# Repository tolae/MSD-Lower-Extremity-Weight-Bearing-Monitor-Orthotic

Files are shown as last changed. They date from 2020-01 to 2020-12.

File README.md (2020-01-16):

# MSD Lower Extremity Weight Bearing Monitor Orthotic

## Overview
Individuals with injury to the lower extremities often go through a type of physical therapy called gait training in which the ability to stand and walk may be improved. Depending on pain control and prescribed weight bearing status (non, toe touch, touchdown, partial, and full/weight bearing as tolerated), patients will gradually place more weight on the injured leg. However, at this time physical therapists have little ability to measure exactly how much weight a patient is bearing.
 
Many orthopedic patients who are recently going through the gait training process struggle with controlling how much weight to bear on a leg recovering from injury. Without proper monitoring, patients often exceed their prescribed weight bearing status which could result in delayed healing, further injury, added frustration, and added financial burden. Determining whether a patient is truly compliant to their weight bearing orders can be difficult for doctors, physical therapists, and patients without accurate readings and progress of the injury. The device proposed here would allow for improved accuracy and weight bearing compliance of the patient’s lower extremities. This could also improve patient motivation and frustration, as progress should be tracked and maintained much more easily.
 
There has been no prior work done with this project.
 
This project would aim to develop and build a working orthotic prototype which could improve the weight bearing compliance and accuracy for leg orthotics while notifying the patient with alerts on whether they are putting too much weight on their foot during therapy.  Notification will also be relayed to the Physical Therapist such that they can direct the patient regarding weight bearing during the physical therapy process.  
 
Strong Memorial Hospital would like their physical therapy staff to be able to use this product with their orthopedic patients during physical therapy sessions within the acute care setting. This will allow physical therapists to more accurately educate patients regarding their weight bearing status, improving patient compliance and decreasing risk of complications after injury.

## Sponsers
Strong Memorial Hospital<br/>
Austin Crane<br/>
Alyssa Reome<br/>

## Workers
Braedon Williams, Bio-Medical Engineer, bpw3109@rit.edu<br/>
Daniel Capra, Eletrical Engineer, dac3781@rit.edu<br/>
Kevin Jones, Industrial Systems Engineer, kmj2243@rit.edu<br/>
Raphael Luo, Eletrical Engineer, jxl6725@rit.edu<br/>
Ethan Tola, Computer Engineer, ext9285@rit.edu<br/>

## Documentation
Documentation for this project can be found on (Confluence)[https://wiki.rit.edu/display/P20016/Project+Overview]. This is a live wiki page that is under construction.

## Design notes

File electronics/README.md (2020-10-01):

# MSD Eletronic Files
All the schematics and designs were done using Cadence Orcad 17.2. The files
in this directory was put under source control for ease of multi-tasking and
reducing the number of redudant work to make the same custom footprints.

## Important Directiories
 - <b>custom_parts</b>: Contains the custom components and pcb footprints
 required for layout.
 - <b>extenstion_1</b>: Contains the schematic and layout focusing on the first
 extenstion for the footpad.
 - <b>imported_parts</b>: Contains footprints and pads for external components
 such as the TMUX1109.
 - <b>main</b>: Contains the schematic and layout focusing on the primary
 footpad that will interface directly with the Arduino Nano.
 - <b>wiring_complete</b>: Contains the schematics for a complete wiring
 diagram of both the Arduino Nano and the Arduino Mega. This cannot be used for
 layout as there are no footprints associated with the parts.

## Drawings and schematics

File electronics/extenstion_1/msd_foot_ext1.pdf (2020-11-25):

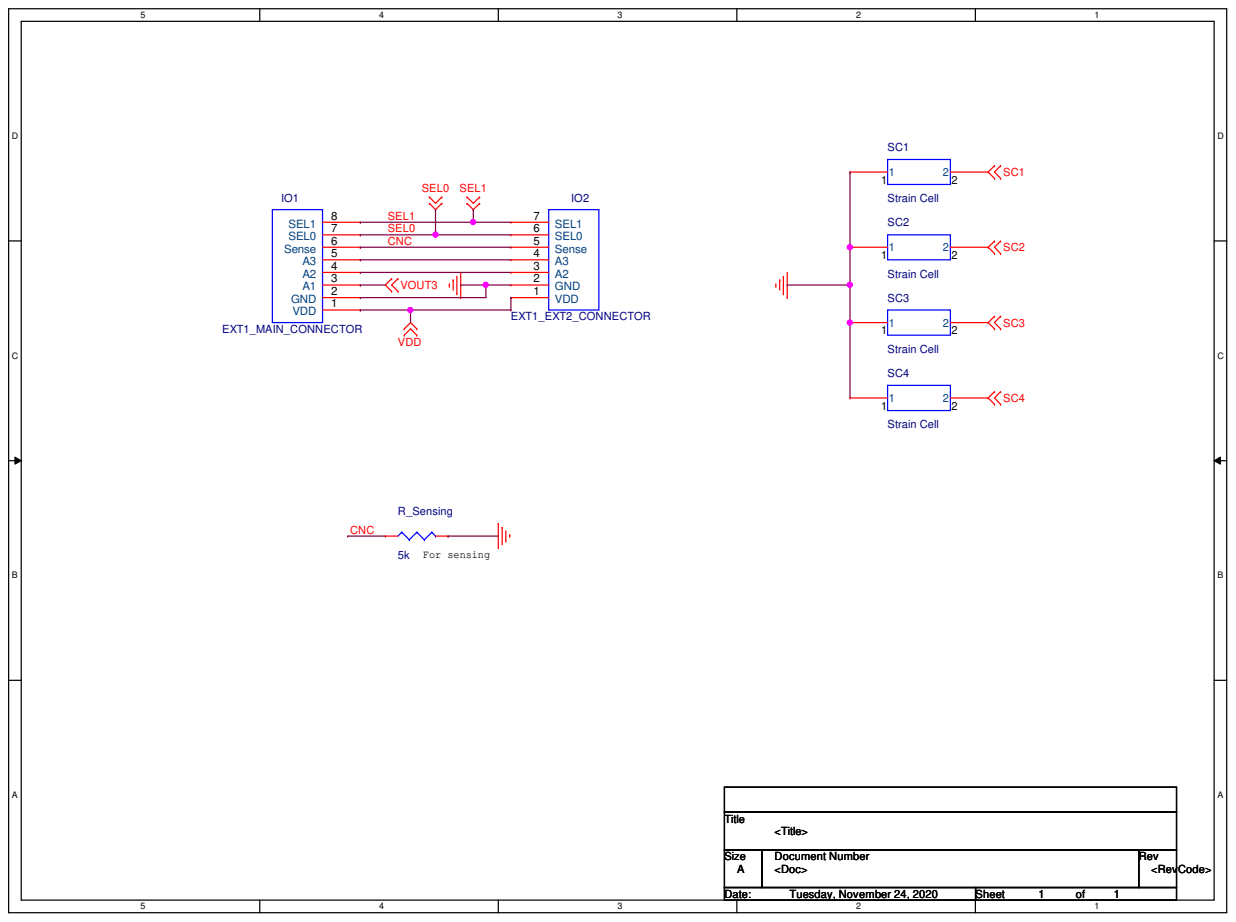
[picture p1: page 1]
For sensing; VDD; VOUT3; SEL0 SEL1; Title; Size; Document Number; Rev; Date:; Sheet; <Doc>; <RevCode>; <Title>; 1Tuesday, November 24, 2020; Strain Cell; EXT1_EXT2_CONNECTOR; Sense 5; GND 2; SEL0 6; SEL1 7; VDD 1; EXT1_MAIN_CONNECTOR; 1 GND; 5 Sense; 6 SEL0; 7 SEL1; R_Sensing; CNC; SEL1 SEL0 CNC

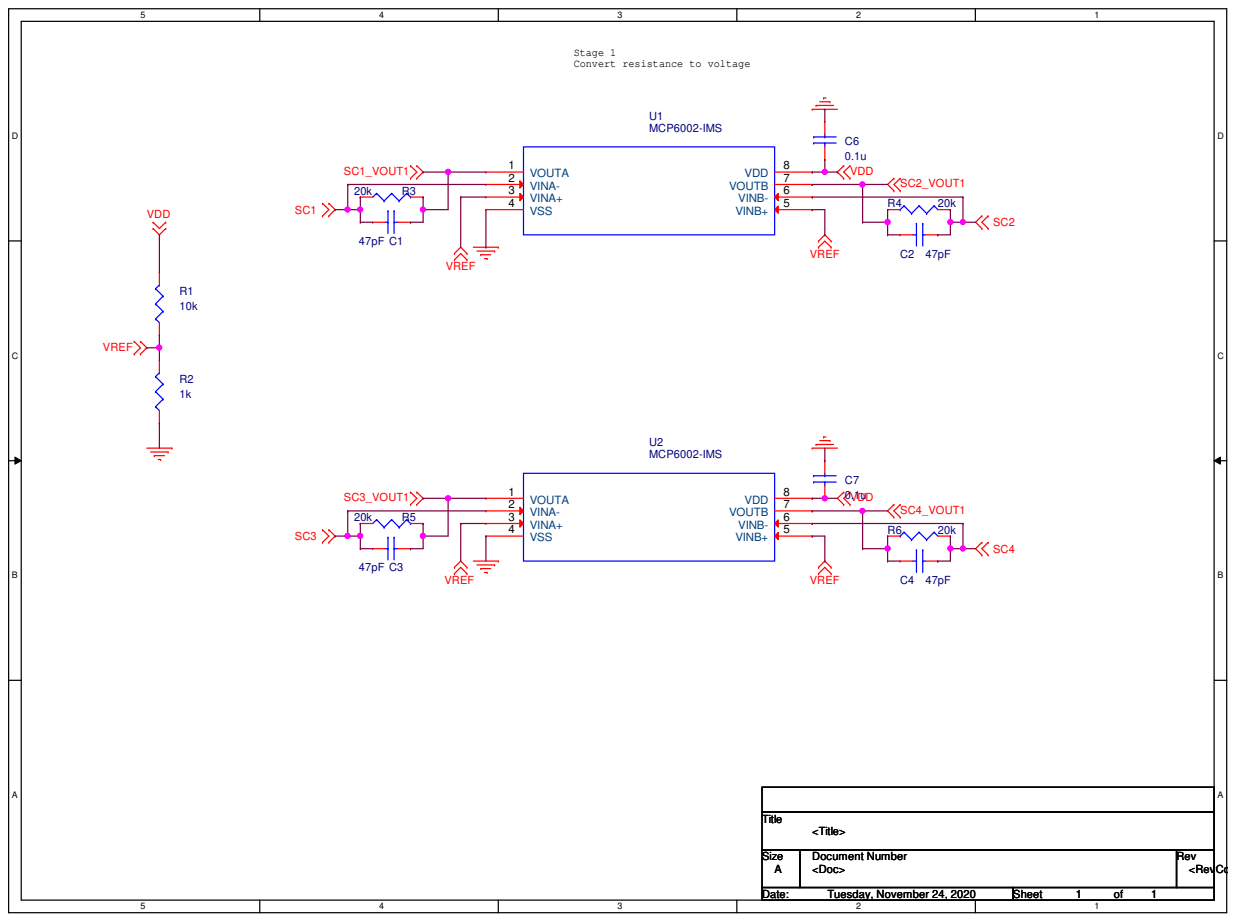
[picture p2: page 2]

Stage 1
Convert resistance to voltage

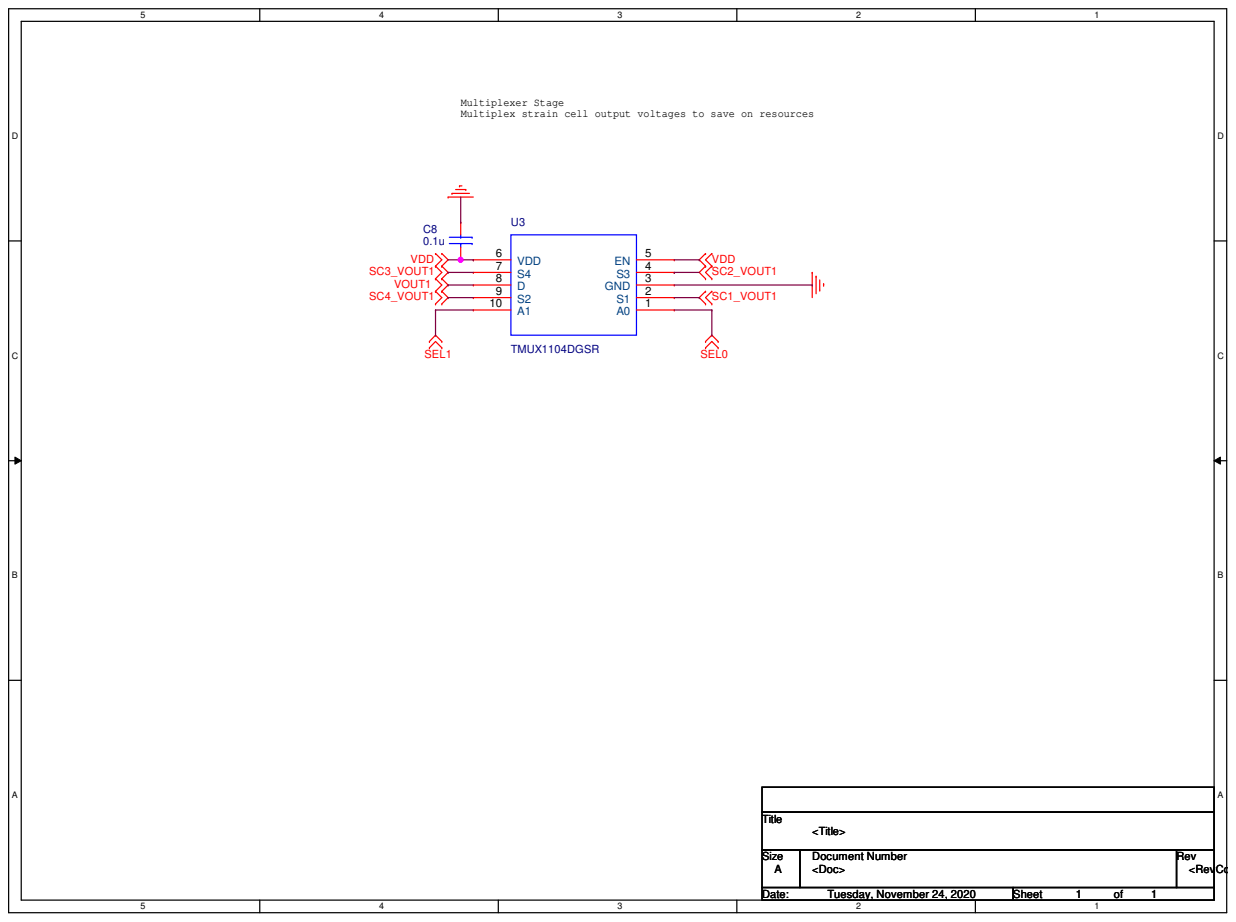
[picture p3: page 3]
SC1_VOUT1; SC2_VOUT1; SC4_VOUT1; SC3_VOUT1; VDD; SEL1; SEL0; VOUT1; Title; Size; Document Number; Rev; Date:; Sheet; <Doc>; <RevCo; <Title>; 1Tuesday, November 24, 2020; TMUX1104DGSR; 2 GND; 5 VDD 6

Multiplexer Stage
Multiplex strain cell output voltages to save on resources

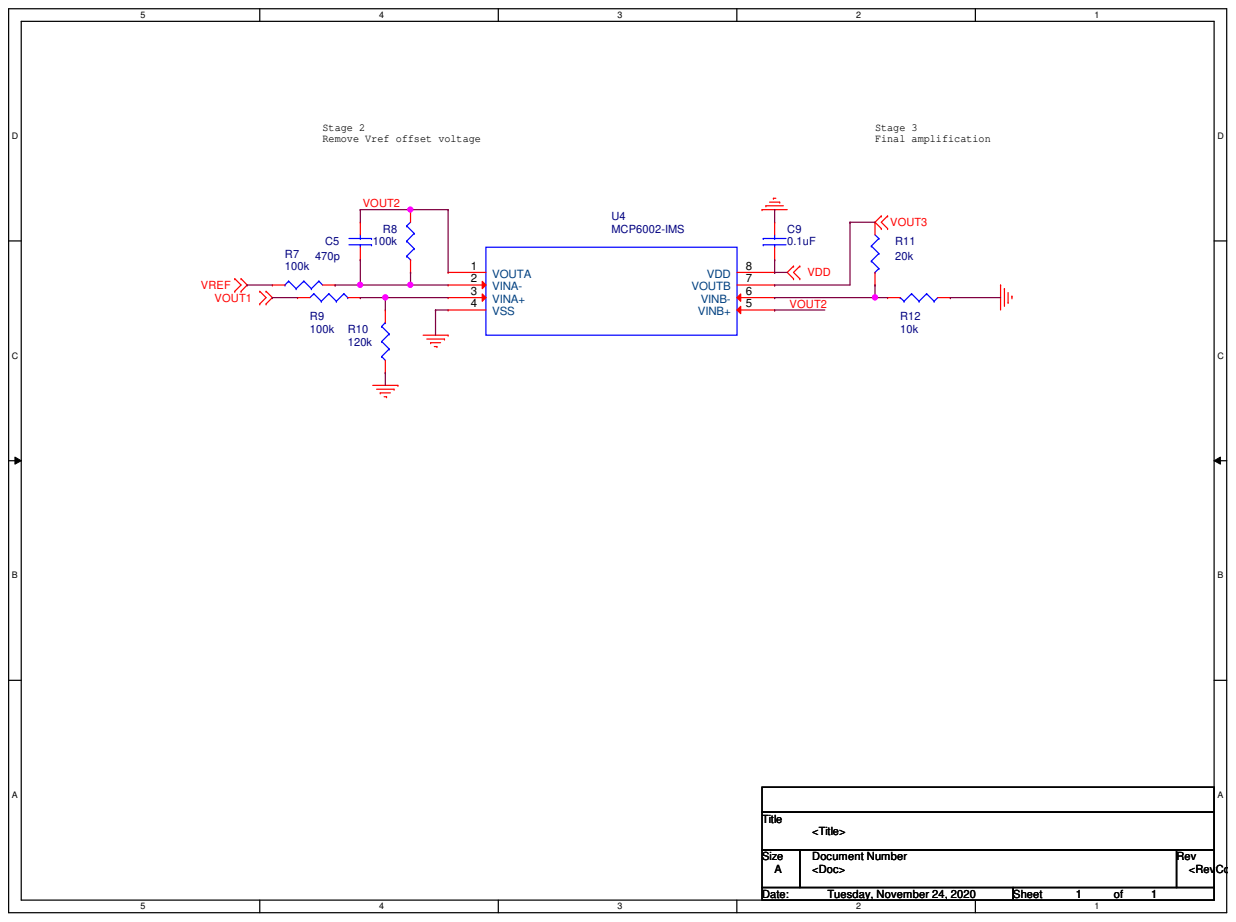
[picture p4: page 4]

Stage 2
Remove Vref offset voltage

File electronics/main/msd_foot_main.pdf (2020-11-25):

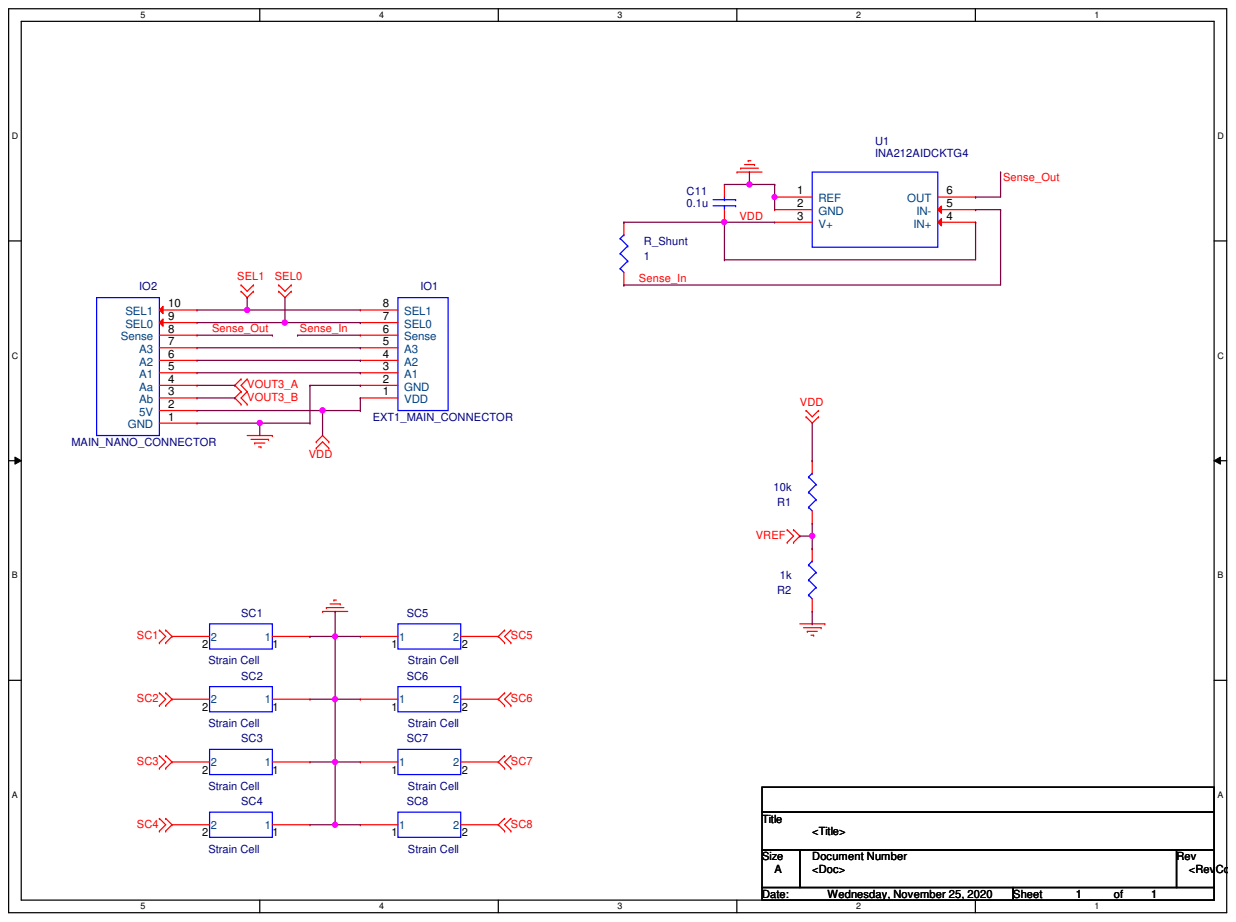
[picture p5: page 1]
VOUT3_B; VOUT3_A; SEL1 SEL0; VDD; VREF; Title; Size; Document Number; Rev; Date:; Sheet; <Doc>; <RevCo; <Title>; 1Wednesday, November 25, 2020; Strain Cell; U1 INA212AIDCKTG4; REF 1 GND 2; 5 OUT; MAIN_NANO_CONNECTOR; GND; 7 Sense; 8 SEL0; 9 SEL1; EXT1_MAIN_CONNECTOR; VDD 1; GND 2; Sense 6; SEL0 7; SEL1 8; R_Shunt 1; Sense_Out; Sense_In

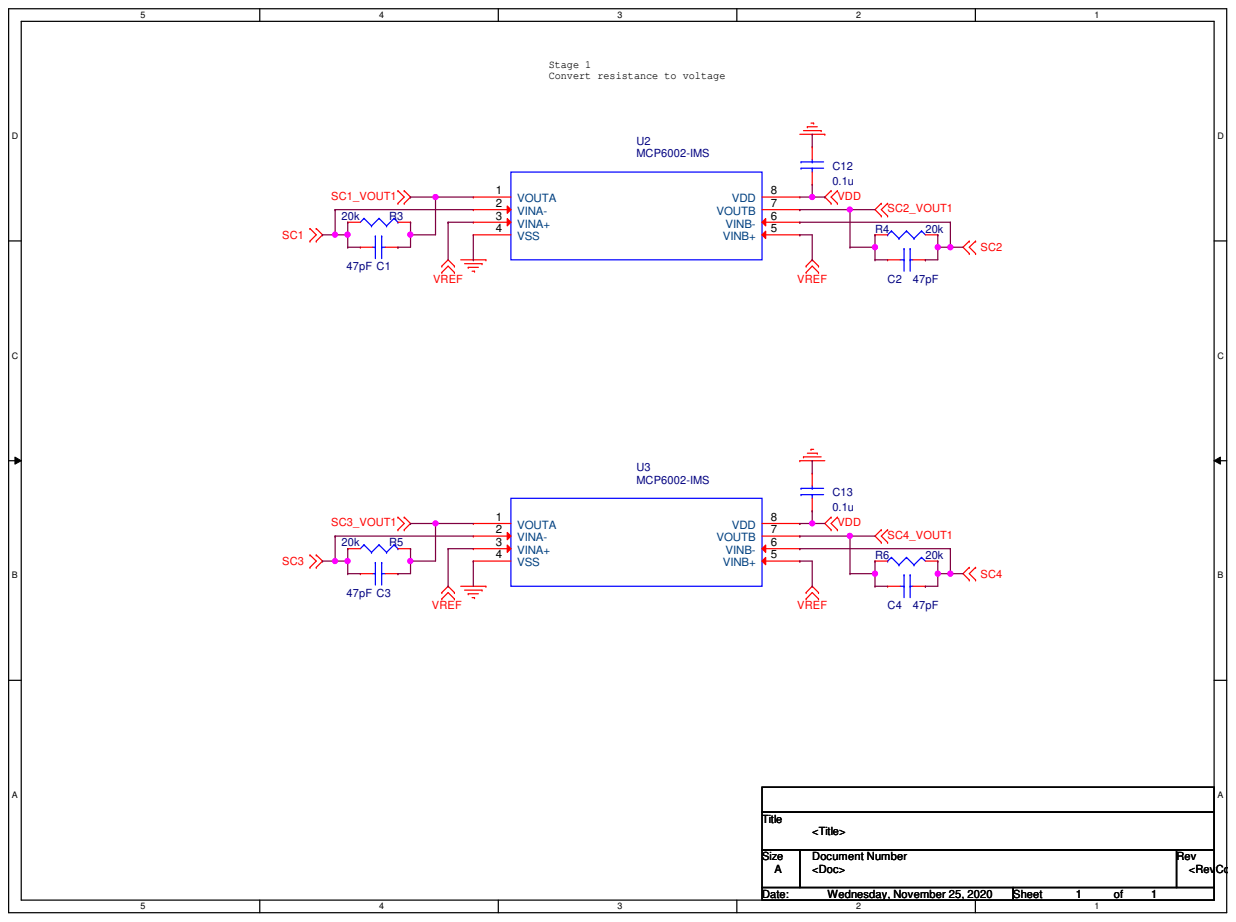
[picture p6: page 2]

Stage 1
Convert resistance to voltage

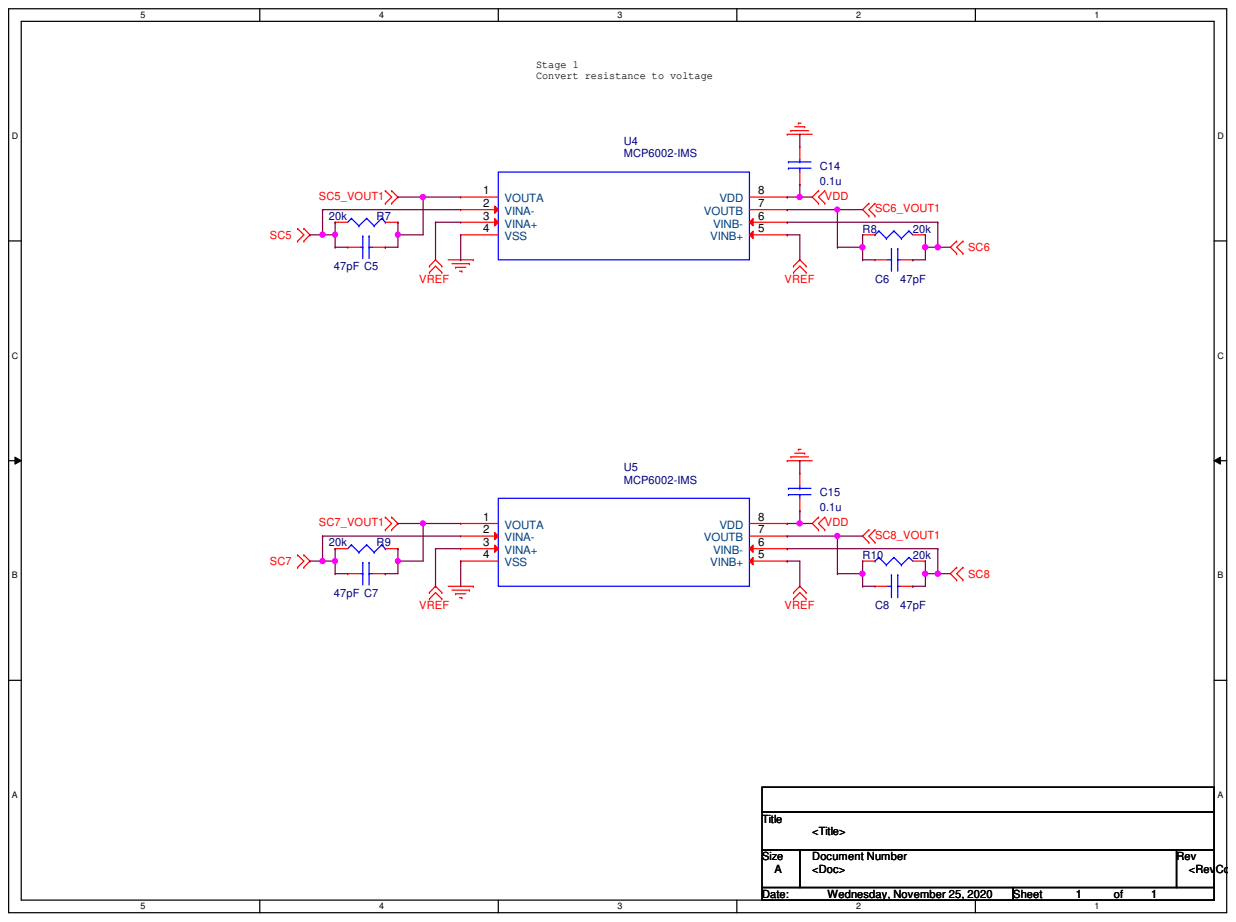
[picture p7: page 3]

Stage 1
Convert resistance to voltage

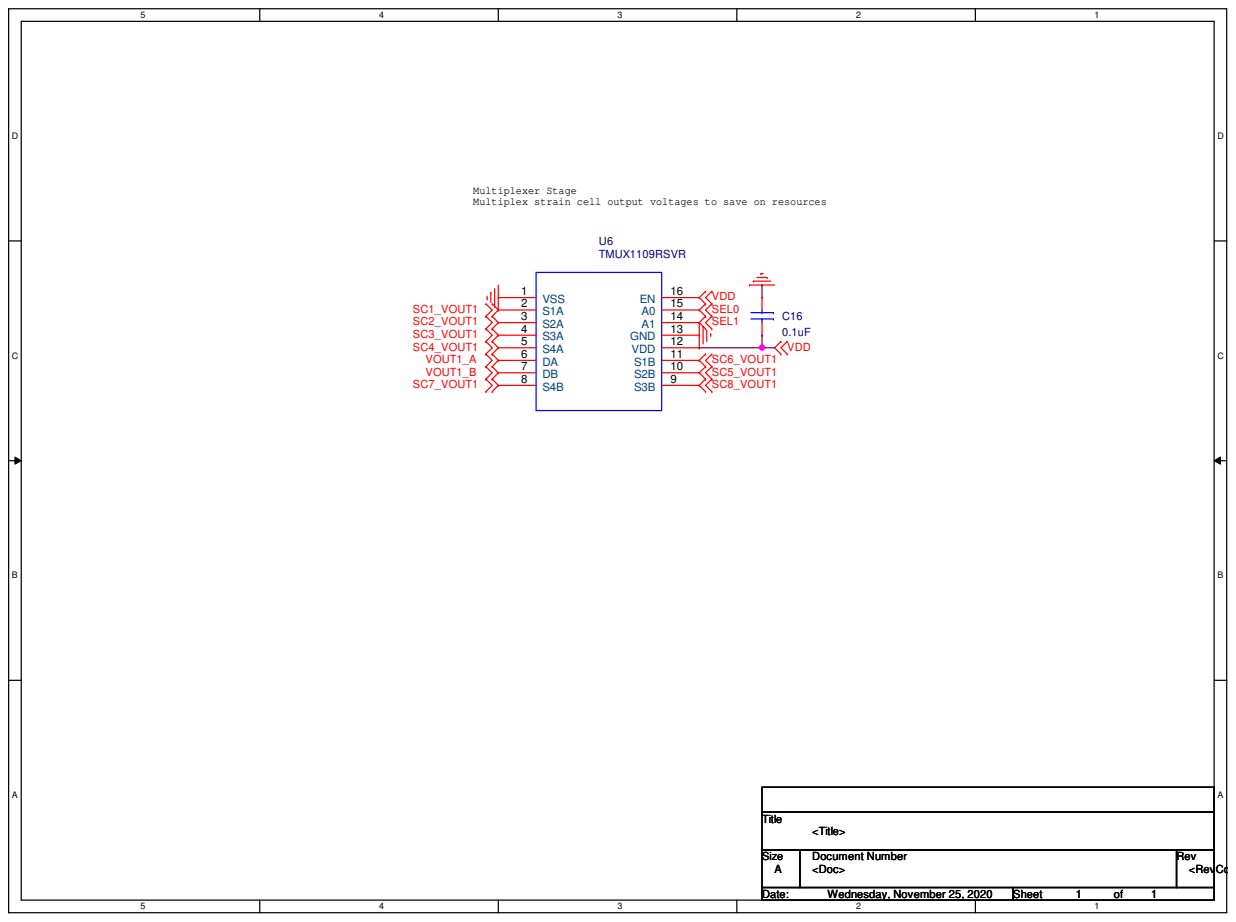
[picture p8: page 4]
SC1_VOUT1; SC6_VOUT1; SC2_VOUT1; SC5_VOUT1; SC3_VOUT1; SC8_VOUT1; SC4_VOUT1; SC7_VOUT1; SEL0 SEL1; VOUT1_B; VOUT1_A; VDD; Title; Size; Document Number; Rev; Date:; Sheet; <Doc>; <RevCo; <Title>; 1Wednesday, November 25, 2020; U6 TMUX1109RSVR; VSS 1 S1A 2 S2A 3 S3A 4 S4A 5 DA 6 DB 7; 11 VDD; 12 GND

Multiplexer Stage
Multiplex strain cell output voltages to save on resources

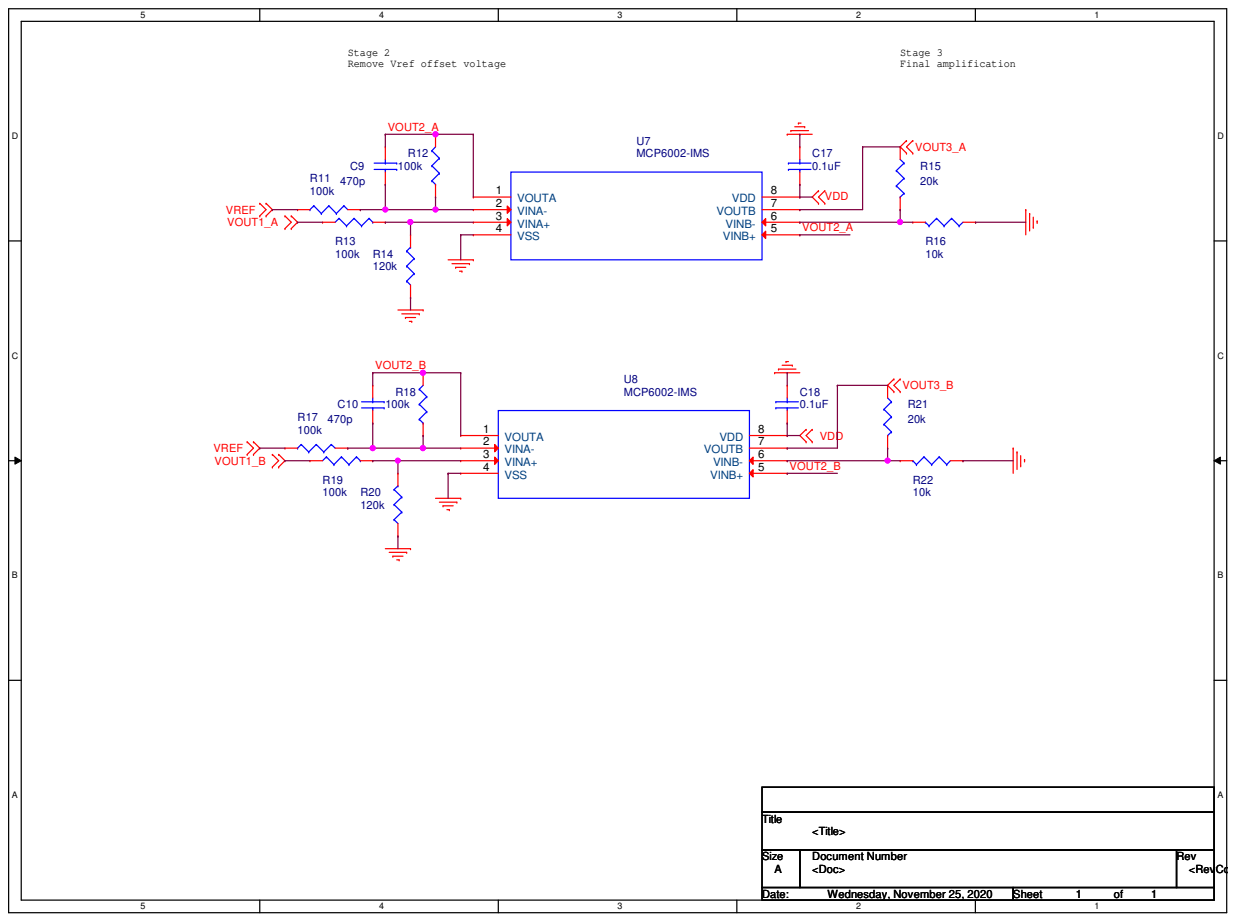
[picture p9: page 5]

Stage 2
Remove Vref offset voltage

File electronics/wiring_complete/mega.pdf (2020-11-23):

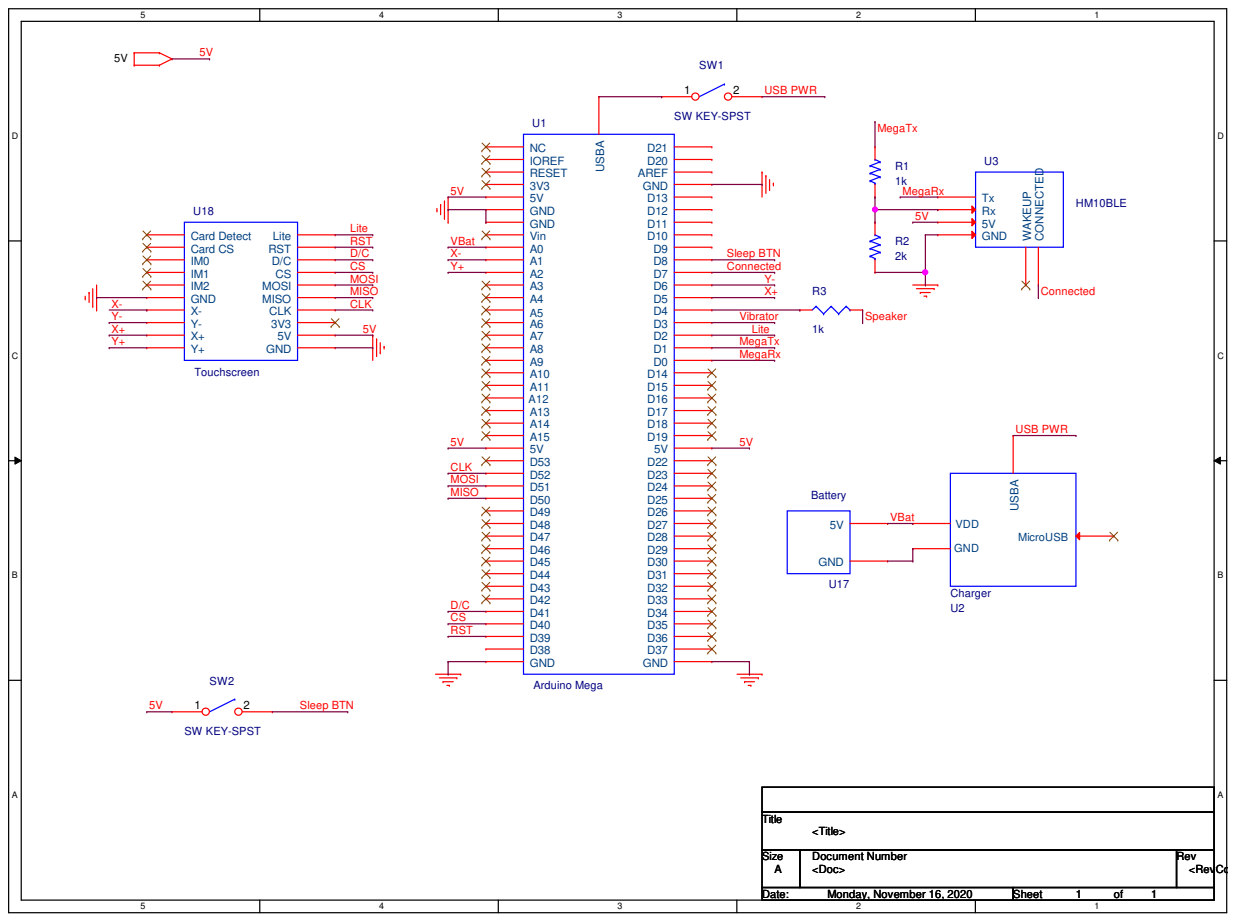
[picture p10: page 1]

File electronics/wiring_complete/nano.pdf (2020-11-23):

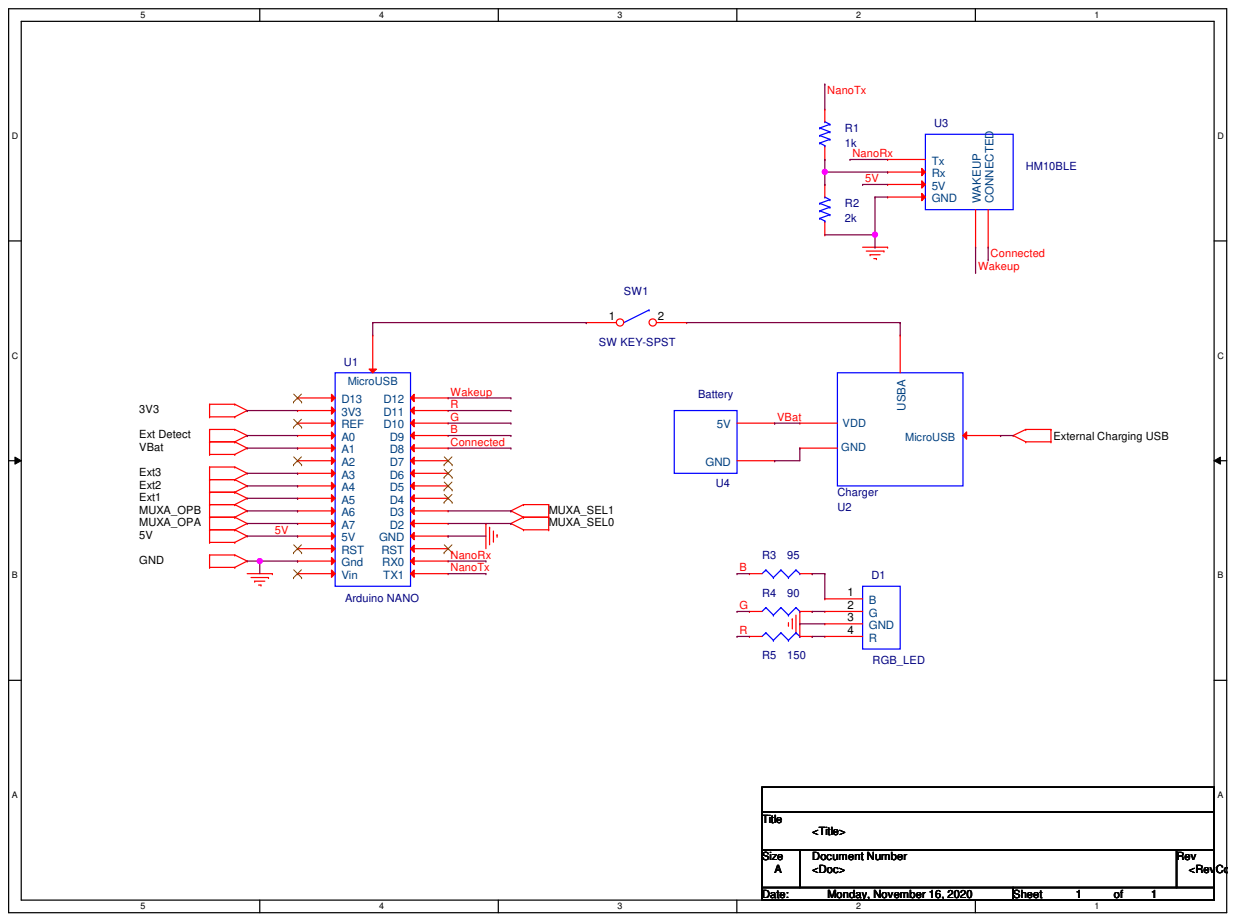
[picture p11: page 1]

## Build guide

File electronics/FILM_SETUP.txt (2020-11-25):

axlFilmCreate( "OUTLINE" ?negative nil ?undefineLineWidth 0.1270 ?sequence 12 
	?rotation 0 ?xOffset 0.0000 ?yOffset 0.0000 ?shapeBoundingBox 2.5400 ?mirrored nil ?fullContact nil 
	?suppressUnconnectPads nil ?drawMissingPadApertures nil ?useApertureRotation nil 
	?suppressShapeFill nil ?vectorBasedPad t ?drawHolesOnly nil 
	?domains '(ipc2581 pdf artwork visibility ) ?ipc2581 '() 
	?layers '("BOARD GEOMETRY/DESIGN_OUTLINE" ))
axlFilmCreate( "SILKSCREEN_TOP" ?negative nil ?undefineLineWidth 0.1270 ?sequence 11 
	?rotation 0 ?xOffset 0.0000 ?yOffset 0.0000 ?shapeBoundingBox 2.5400 ?mirrored nil ?fullContact nil 
	?suppressUnconnectPads nil ?drawMissingPadApertures nil ?useApertureRotation nil 
	?suppressShapeFill nil ?vectorBasedPad t ?drawHolesOnly nil 
	?domains '(ipc2581 pdf artwork visibility ) ?ipc2581 '(doc ) 
	?layers '("REF DES/SILKSCREEN_TOP" "PACKAGE GEOMETRY/SILKSCREEN_TOP" "COMPONENT VALUE/SILKSCREEN_TOP" "BOARD GEOMETRY/SILKSCREEN_TOP" "BOARD GEOMETRY/DESIGN_OUTLINE" ))
axlFilmCreate( "PASTEMASK_BOT" ?negative nil ?undefineLineWidth 0.1270 ?sequence 10 
	?rotation 0 ?xOffset 0.0000 ?yOffset 0.0000 ?shapeBoundingBox 2.5400 ?mirrored nil ?fullContact nil 
	?suppressUnconnectPads nil ?drawMissingPadApertures nil ?useApertureRotation nil 
	?suppressShapeFill nil ?vectorBasedPad t ?drawHolesOnly nil 
	?domains '(ipc2581 pdf artwork visibility ) ?ipc2581 '(soldermask ) 
	?layers '("VIA CLASS/PASTEMASK_BOTTOM" "PIN/PASTEMASK_BOTTOM" "PACKAGE GEOMETRY/PASTEMASK_BOTTOM" "DRC ERROR CLASS/PASTEMASK_BOTTOM" "BOARD GEOMETRY/DESIGN_OUTLINE" ))
axlFilmCreate( "SOLDERMASK_BOT" ?negative nil ?undefineLineWidth 0.1270 ?sequence 9 
	?rotation 0 ?xOffset 0.0000 ?yOffset 0.0000 ?shapeBoundingBox 2.5400 ?mirrored nil ?fullContact nil 
	?suppressUnconnectPads nil ?drawMissingPadApertures nil ?useApertureRotation nil 
	?suppressShapeFill nil ?vectorBasedPad t ?drawHolesOnly nil 
	?domains '(ipc2581 pdf artwork visibility ) ?ipc2581 '(soldermask ) 
	?layers '("VIA CLASS/SOLDERMASK_BOTTOM" "PIN/SOLDERMASK_BOTTOM" "PACKAGE GEOMETRY/SOLDERMASK_BOTTOM" "DRC ERROR CLASS/SOLDERMASK_BOTTOM" "BOARD GEOMETRY/SOLDERMASK_BOTTOM" "BOARD GEOMETRY/DESIGN_OUTLINE" ))
axlFilmCreate( "PASTEMASK_TOP" ?negative nil ?undefineLineWidth 0.1270 ?sequence 8 
	?rotation 0 ?xOffset 0.0000 ?yOffset 0.0000 ?shapeBoundingBox 2.5400 ?mirrored nil ?fullContact nil 
	?suppressUnconnectPads nil ?drawMissingPadApertures nil ?useApertureRotation nil 
	?suppressShapeFill nil ?vectorBasedPad t ?drawHolesOnly nil 
	?domains '(ipc2581 pdf artwork visibility ) ?ipc2581 '(soldermask ) 
	?layers '("VIA CLASS/PASTEMASK_TOP" "PIN/PASTEMASK_TOP" "PACKAGE GEOMETRY/PASTEMASK_TOP" "DRC ERROR CLASS/PASTEMASK_TOP" "BOARD GEOMETRY/DESIGN_OUTLINE" ))
axlFilmCreate( "SOLDERMASK_TOP" ?negative nil ?undefineLineWidth 0.1270 ?sequence 7 
	?rotation 0 ?xOffset 0.0000 ?yOffset 0.0000 ?shapeBoundingBox 2.5400 ?mirrored nil ?fullContact nil 
	?suppressUnconnectPads nil ?drawMissingPadApertures nil ?useApertureRotation nil 
	?suppressShapeFill nil ?vectorBasedPad t ?drawHolesOnly nil 
	?domains '(ipc2581 pdf artwork visibility ) ?ipc2581 '(soldermask ) 
	?layers '("VIA CLASS/SOLDERMASK_TOP" "PIN/SOLDERMASK_TOP" "PACKAGE GEOMETRY/SOLDERMASK_TOP" "DRC ERROR CLASS/SOLDERMASK_TOP" "BOARD GEOMETRY/SOLDERMASK_TOP" "BOARD GEOMETRY/DESIGN_OUTLINE" ))
axlFilmCreate( "SILKSCREEN_BOT" ?negative nil ?undefineLineWidth 0.1270 ?sequence 6 
	?rotation 0 ?xOffset 0.0000 ?yOffset 0.0000 ?shapeBoundingBox 2.5400 ?mirrored nil ?fullContact nil 
	?suppressUnconnectPads nil ?drawMissingPadApertures nil ?useApertureRotation nil 
	?suppressShapeFill nil ?vectorBasedPad t ?drawHolesOnly nil 
	?domains '(ipc2581 pdf artwork visibility ) ?ipc2581 '(doc ) 
	?layers '("REF DES/SILKSCREEN_BOTTOM" "PACKAGE GEOMETRY/SILKSCREEN_BOTTOM" "BOARD GEOMETRY/SILKSCREEN_BOTTOM" "BOARD GEOMETRY/DESIGN_OUTLINE" ))
axlFilmCreate( "ASSEMBLY" ?negative nil ?undefineLineWidth 0.1270 ?sequence 4 
	?rotation 0 ?xOffset 0.0000 ?yOffset 0.0000 ?shapeBoundingBox 2.5400 ?mirrored nil ?fullContact nil 
	?suppressUnconnectPads nil ?drawMissingPadApertures nil ?useApertureRotation nil 
	?suppressShapeFill nil ?vectorBasedPad t ?drawHolesOnly nil 
	?domains '(ipc2581 pdf artwork visibility ) ?ipc2581 '(doc ) 
	?layers '("REF DES/ASSEMBLY_TOP" "PIN/TOP" "PACKAGE GEOMETRY/ASSEMBLY_TOP" "DRAWING FORMAT/OUTLINE" "DRAWING FORMAT/TITLE_BLOCK" "DRAWING FORMAT/TITLE_DATA" "DRAWING FORMAT/REVISION_BLOCK" "DRAWING FORMAT/REVISION_DATA" "BOARD GEOMETRY/DESIGN_OUTLINE" ))
axlFilmCreate( "FAB" ?negative nil ?undefineLineWidth 0.1270 ?sequence 3 
	?rotation 0 ?xOffset 0.0000 ?yOffset 0.0000 ?shapeBoundingBox 2.5400 ?mirrored nil ?fullContact nil 
	?suppressUnconnectPads nil ?drawMissingPadApertures nil ?useApertureRotation nil 
	?suppressShapeFill nil ?vectorBasedPad t ?drawHolesOnly nil 
	?domains '(ipc2581 pdf artwork visibility ) ?ipc2581 '(doc ) 
	?layers '("MANUFACTURING/XSECTION_CHART" "MANUFACTURING/NCLEGEND-1-2" "DRAWING FORMAT/TITLE_DATA" "DRAWING FORMAT/TITLE_BLOCK" "DRAWING FORMAT/REVISION_DATA" "DRAWING FORMAT/REVISION_BLOCK" "DRAWING FORMAT/OUTLINE" "DRAWING FORMAT/DRAWING_ORIGIN" "BOARD GEOMETRY/DIMENSION" "BOARD GEOMETRY/DESIGN_OUTLINE" ))

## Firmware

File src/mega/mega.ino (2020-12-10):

/***************************************************
	Example showing a list of elements, some enabled, some disabled some touch enabled

	NOTE: screeen rotation is set to 270 degrees. Don't worry, the touchscreen will map
	correctly.

	Uses Adafruit TFT library for the example:
	Written by Limor Fried/Ladyada for Adafruit Industries.
	MIT license, all text above must be included in any redistribution
 ****************************************************/

/** NOT FOR USE WITH THE TOUCH SHIELD, ONLY FOR THE BREAKOUT! **/


// These are the four touchscreen analog pins
#define YP A2  // must be an analog pin, use "An" notation!
#define XM A1  // must be an analog pin, use "An" notation!
#define YM 6   // can be a digital pin
#define XP 5   // can be a digital pin

// This is calibration data for the raw touch data to the screen coordinates
#define TS_MINX 150
#define TS_MINY 100
#define TS_MAXX 900
#define TS_MAXY 900


// The display uses hardware SPI, plus #9 & #10
#define TFT_CS 10
#define TFT_DC 9
#define TFT_RST 8 // RST can be set to -1 if you tie it to Arduino's reset

#define VIRBATOR_PWM_PIN 3

#define GUICONFIG_H_

#include <Adafruit_GFX.h>    // Core graphics library
#include <SPI.h>
#include <Adafruit_HX8357.h>
#include <TouchScreen.h>
#include "inc/mega.h"
#include "inc/screen_manager.h"
#include "inc/keypad_screen.h"
#include "inc/home_screen.h"
#include "inc/settings_screen.h"
#include "inc/timer.h"

// Use hardware SPI (on Uno, #13, #12, #11) and the above for CS/DC
Adafruit_HX8357 tft = Adafruit_HX8357(TFT_CS, TFT_DC, TFT_RST);

// For better pressure precision, we need to know the resistance
// between X+ and X- Use any multimeter to read it
// For the one we're using, its 300 ohms across the X plate
TouchScreen ts = TouchScreen(XP, YP, XM, YM, 300);

// Setup the gui model
// needs reference to the tft and the touchscreen
Gui gui(&tft, &ts, 0, 0, tft.height(), tft.width());

const Screen* SCREENS[] = 
{
  new KeypadScreen(0, 0, TS_MAXX - TS_MINX, TS_MAXY - TS_MINY),
  new HomeScreen(0, 0, TS_MAXX - TS_MINX, TS_MAXY - TS_MINY),
  new SettingsScreen(0, 0, TS_MAXX - TS_MINX, TS_MAXY - TS_MINY)
};

Volume speaker_vol;
VibratorMotor vib_motor(VIRBATOR_PWM_PIN, 1);

ScreenManager* screen_manager = new ScreenManager();

void setup(void) {
	Serial.begin(115200);
	while(!Serial);
	Serial.println("Gui Widgets test!");
    /* Initialize hardware */
	speaker_vol.setMasterVolume(1);
	
	tft.begin();
	// in multiples of 90 only
	gui.setRotation(270);

	for (int i = 0; i < sizeof(SCREENS) / sizeof(char*); i++)
	{
		Screen* screen = SCREENS[i];
		screen->visible(false);
		gui.addChild(screen);
	}
	screen_manager->init_screen(SCREENS[1]);
	
	gui.draw();

	return;
}

void loop()
{
	// this has to be called to keep the system up to date
	gui.update();
	screen_manager->update();

	return;
}

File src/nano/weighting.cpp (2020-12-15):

#include "inc/weighting.h"
#include "inc/convolution.h"

/** Defines **/

/* Defines for extender board connection logic */
#define CONNECTIONS_READING_ANALOG_PIN A0
#define EXT_ANALOG_PER_CONNECTION 205
/***********************************************/

/* Defines for sensor ids and sensor count logic */
#define BASE_SENSOR_ID_MAX 2 // Modified from 8 as we only have 2 sensors for demo.
#define ONE_EXT_SENSOR_ID_MAX 12
#define TWO_EXT_SENSOR_ID_MAX 16
#define THREE_EXT_SENSOR_ID_MAX 20

#define SENSOR_MAX 20
#define SENSOR_HISTORY 16
#define SENSORS_PER_EXT 4
/*************************************************/

/* Defines for sensor pin locations */
/* Analog Pins */
#define MUXA_OPA_ANALOG_PIN A7
#define MUXA_OPB_ANALOG_PIN A6
#define EXT1_ANALOG_PIN A5
#define EXT2_ANALOG_PIN A4
#define EXT3_ANALOG_PIN A3

/* Digital Pins */
#define MUXA_SELECT0 2
#define MUXA_SELECT1 3

#define MUXA_SELECT0_MASK 0x01
#define MUXA_SELECT1_MASK 0x02
/*************************************************/

/* Defines for sensor data logic */
#define MAX_AVERAGE_CNT 1 // Modified from 4 as we only have 2 sensors for demo.
/*********************************/

/* Enumeration for how many connector boards are attached (and supported) */
typedef enum CONNECTED_SENSORS
{
	NO_EXT = 0,
	ONE_EXT,
	TWO_EXT,
	THREE_EXT
} connections_t;

/** Array of sensor readings
 * 
 * The first array corresponds to the individual 20 sensors.
 * The second array corresponds to the history for that particular sensor.
 */
uint16_t sensor_weights[SENSOR_MAX][SENSOR_HISTORY];
uint8_t sensor_weights_curr_index = 0;

/* Global variable that holds the number of connections */
connections_t connections = NO_EXT;

/* Updates the connections variable with the current number of attached exts */
void _check_connections();

/* Updates the particular sensor */
void _update_sensor(uint8_t sensor);

/** Computes a single reading and returns a weight calculation.
 * 
 * Needs to be ran SENSOR_HISTORY times before valid/useful values come out.
*/
uint16_t update_weights()
{
	uint8_t i;
	uint8_t j;
	uint8_t k;
	uint32_t average = 0;
	uint32_t max_averages[MAX_AVERAGE_CNT] = {0};
	/* Current unused for demo purposes */
	// _check_connections();

	/** The base pad has 8 connections (read at twice the speed), with each ext
	 * adding 4 sensors.
	 */
	for (i = 0; i < BASE_SENSOR_ID_MAX + connections * SENSORS_PER_EXT; i++)
	{
		_update_sensor(i);

		/* With the updated sensor, average out the last 16 readings. */
		for (j = 0; j < SENSOR_HISTORY; j++)
		{
			average += sensor_weights[i][j];
		}
		average /= SENSOR_HISTORY;
		
		/* Store all the max averages */
		for (k = 0; k < MAX_AVERAGE_CNT; k++)
		{
			if (max_averages[k] < average)
			{
				max_averages[k] = average;
			}
		}
	}
	sensor_weights_curr_index = (++sensor_weights_curr_index) % SENSOR_HISTORY;

	/* Compute the final average */
	average = 0;
	for (k = 0; k < MAX_AVERAGE_CNT; k++)
	{
		average += max_averages[k];
	}
	average /= MAX_AVERAGE_CNT;

	return average;
}

void _check_connections()
{
	uint16_t divider = analogRead(CONNECTIONS_READING_ANALOG_PIN);
	if (divider > EXT_ANALOG_PER_CONNECTION*4)
	{
		/* 4 extentions */
	}
	else if (divider > EXT_ANALOG_PER_CONNECTION*3)
	{
		connections = THREE_EXT;
	}
	else if (divider > EXT_ANALOG_PER_CONNECTION*2)
	{
		connections = TWO_EXT;
	}
	else if (divider > EXT_ANALOG_PER_CONNECTION)
	{
		connections = ONE_EXT;
	}
	else
	{
		connections = NO_EXT;
	}
}

void _update_sensor(uint8_t sensor)
{
	uint8_t mux_sel;
	if (sensor < BASE_SENSOR_ID_MAX)
	{
		/** The base pad reads two sensors at a time. The pairs of sensors will
		 * be next to each other in the array.
		 * 
		 * Set the mux for the given pair of sensors and read them.
		 */
		/** No longer used as demo circuit doesn't have multiplexers **/
		/* Sensors come in pairs */
		// mux_sel = sensor / 2;
		// digitalWrite(MUXA_SELECT0, mux_sel & MUXA_SELECT0_MASK);
		// digitalWrite(MUXA_SELECT1, mux_sel & MUXA_SELECT1_MASK);
		/* Allow muxs to stabilize the signal */
		// delay(1);

		if (sensor % 2)
		{
			sensor_weights[sensor][sensor_weights_curr_index] = analogRead(MUXA_OPA_ANALOG_PIN);
		}
		else
		{
			sensor_weights[sensor][sensor_weights_curr_index] = analogRead(MUXA_OPB_ANALOG_PIN);
		}
	}
	else
	{
		/** The extention pads are read one at a time.
		 * 
		 * Set the mux for the given sensor and read them.
		 */
		mux_sel = sensor % SENSORS_PER_EXT;
		digitalWrite(MUXA_SELECT0, mux_sel & MUXA_SELECT0_MASK);
		digitalWrite(MUXA_SELECT1, mux_sel & MUXA_SELECT1_MASK);
		delay(1); // Allow muxs to stabilize the signal

		if (sensor < ONE_EXT_SENSOR_ID_MAX)
		{
			sensor_weights[sensor][sensor_weights_curr_index] = analogRead(EXT1_ANALOG_PIN);
		}
		else if (sensor < TWO_EXT_SENSOR_ID_MAX)
		{
			sensor_weights[sensor][sensor_weights_curr_index] = analogRead(EXT2_ANALOG_PIN);
		}
		else if (sensor < THREE_EXT_SENSOR_ID_MAX)
		{
			sensor_weights[sensor][sensor_weights_curr_index] = analogRead(EXT3_ANALOG_PIN);
		}
	}
}

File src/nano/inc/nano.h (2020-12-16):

#ifndef _NANO_H
#define _NANO_H

#define DEBUG_WITH_ALTSOFT

#define BLUETOOTH_MOD_CONNECTION_PIN 7

#define LED_R_PIN 11
#define LED_G_PIN 10
#define LED_B_PIN 9

const uint32_t LOOP_TIME_DELAY_MS = 50;

#endif

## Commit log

2020-08-31 Created testing framework for hardware.
    These tests will specifically be designed to test particular hardware
    components with potential human intervention. The current design for
    this framework is to have each test have its own firmware that will
    execute on the desired board. The python scripts are there to compile
    and upload each script as well as potentially passing variables to the
    board if required. It will use a json configuration to manage switching
    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
2020-09-05 Refactored and completed new functionality.
    It required a change in how the tests themselves are ran. The base dut
    now contains the methods to compile, upload, and verify the test
    configurations given to it.
    To support multiple duts, a special suffix is used (similar to tests) to
    match the _dut to the _tests suite. This way, its very easy to match the
    board with the test it should execute. Multiple dut configurations will
    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
2020-09-10 Corrected bug when 0 is pressed.
    Do nothing if the current vlaue is 0
2020-09-10 Removed the need for a global screen.
    Callback functions can accept a void * carry which can be used to
    maintain a reference for the current screen. This should be used instead
    of global variables if possible.
2020-09-10 Shifted screen to be GuiElement.
    This lets the primary gui only need to detach a single element (a screen
    in this case) rather than a bunch of elements.
2020-09-10 Created init_screen and refactored switch_screen.
    Switch_screen lost an argument to utilize the internal current screen.
2020-10-01 Added layout projects to github
    [MSD_FOOT_EXT1.DSN, MSD_FOOT_MAIN.DSN]
2020-10-01 Added complete wiring schematics to github.
    [MSD_COMPLETE_WIRING.DSN]
2020-10-01 Added imported parts.
    [dgs10_tex.psm, sot-23-5_mc_mch.psm]
2020-10-01 Added IO connectors for EXT1.
2020-10-01 Implemented IO conenctors to footpad.
    [MSD_FOOT_EXT1.DSN]
2020-10-01 Added import part MCP6002IMS.
    [msop8_mc_mch.psm]
2020-10-01 Added sensors and connectors to main orthotic.
    [MSD_FOOT_MAIN.DSN]
2020-10-01 Fixed minor typo in naming and net aliases.
    [MSD_FOOT_EXT1.DSN, MSD_FOOT_MAIN.DSN]
2020-10-02 Shifted shunt resistor to high side.
    This was as a recommendation of the schematic.
    Added a decoupling 0.1uF capacitors to each IC between VDD and ground.
    Removed the mosfet that controlled power to the sensing circuit.
    [MSD_FOOT_EXT1.DSN, MSD_FOOT_MAIN.DSN]
2020-10-02 Changed capacitors to straight, nonpolar.
    [MSD_FOOT_EXT1.DSN, MSD_FOOT_MAIN.DSN]
2020-10-03 Created strain_cell footprint.
    This also includes the 2mm x 2mm square padstack named smd2mm_2mm.pad.
    [strain_cell.psm]
2020-10-03 Created rect pads for board to board connectors.
2020-10-03 Created extension connectors.
    Created .gitignore to ignore log files produced when using PCB Editor.
    [ext1_ext2_connector.psm, ext1_main_connector.psm]
2020-10-03 Added footprints to connectors and strain cells.
    Created .gitignore to ignore lock files. Note, a user should close OrCad
    before committing as the .opj file might change after closing.
    [MSD_FOOT_EXT1.DSN]
2020-10-03 Started the pcb layout for the extention.
    [extension1.brd]
2020-10-03 First pass at routing.
    Some traces need modifications to get rid of the 90 angles. The board
    must also be squished inward for space.
    [MSD_FOOT_EXT1.DSN, msd_foot_ext1.brd]
2020-10-03 Fixed ground pour and fit boundary to the design.
    [msd_foot_ext1.brd]
2020-10-07 Updated ext1 routing to be skinnier and longer.
    [msd_foot_ext1.brd]
2020-10-07 Created ext2 and ext3 schematics.
    This includes the accompanying connector for them.
    [MSD_FOOT_EXT2.DSN, MSD_FOOT_EXT3.DSN, ext2_ext3_connector.psm]
2020-10-07 Did layouts for ext2 and ext3.
    We should double check these layouts prior to printing.
    [MSD_FOOT_EXT2.DSN, MSD_FOOT_EXT3.DSN, msd_foot_ext2.brd, msd_foot_ext3.brd]
2020-10-09 Created shield for mega to attach tft screen.
    This was a rough first pass but it should be set to print. May be
    expensive to print something this large but yeet.
    [1x08.psm, 1x10.psm, 1x20.psm, 2x18.psm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]
2020-10-09 Added dimensions to each board.
    Fixed ext1 by making it more compact
    [arduino_mega_tft_3p5_shield.brd, msd_foot_ext1.brd, msd_foot_ext2.brd, msd_foot_ext3.brd]
2020-10-09 Fixed missing routes.
    [msd_foot_ext1.brd]
2020-10-09 Prepared ext 1 for printing.
    [msd_foot_ext1-1-2.drl, msd_foot_ext1.brd]
2020-10-13 Finalized expansion board 1 for printing.
    [msd_foot_ext1-1-2.drl, msd_foot_ext1.brd]
2020-10-20 Created sample execution of timer modules.
2020-10-27 Updated hardware to rev 3.
    Test PCB output and it looks good!
    [MSD_FOOT_EXT1.DSN, msd_foot_ext1-1-2.drl, msd_foot_ext1.brd]
2020-11-09 Implemented baseline nano data flow.
    Implemented a state machine to handle the LED components. Each function
    still needs to be written out.
    Putting everything in the main loop for now to ensure it all works. We
    should probably breakout the current weight measurement to a timer so
    the whole loop doesn't have to be delayed. Currently measuring at 20 Hz
    (every 50 ms).
2020-11-16 Updated wiring schematic to reflect all components.
    Exported them as pdfs for ease of viewing
    [MSD_COMPLETE_WIRING.DSN]
2020-11-16 Filled in logic to read in sensors.
    Updated defines and improved comments.
2020-11-16 Added simple testing code for circuit validation.
    This is primarily focusing on being able to read out analog sensor
    values from the pcb and switching. Another test will be used later to
    validate connector boards.
2020-11-17 Fixed bad trace for VDD on ext1 board.
    [msd_foot_ext1.brd]
2020-11-23 Updated nano wiring schematic to include BJTs.
    BJTs were required for the nano to power the LED appropriately without
    damaging the IO pins.
    [MSD_COMPLETE_WIRING.DSN]
2020-11-23 Added vibrator motor class to control strength.
2020-11-23 Switched first gain stage and the multiplexer stage.
    [MSD_FOOT_EXT1.DSN]
2020-11-24 Updated schematics with new shifted mux stage.
    [MSD_FOOT_EXT1.DSN, MSD_FOOT_MAIN.DSN]
2020-11-25 Updated schematics and laid out ext 1.
    Also added FILM_SETUP.txt for future use in all electronics.
    [MSD_FOOT_EXT1.DSN, MSD_FOOT_MAIN.DSN, msd_foot_ext1-1-2.drl, msd_foot_ext1.brd]
2020-11-25 Completed layout for main board.
    All that's left is one last glance over to ensure everything is routed
    and then it can be printed.
    [MSD_FOOT_MAIN.DSN, dck6_tex.psm, main_connector.psm, msd_foot_ext1-1-2.drl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]
2020-11-25 Created pdfs of the schematic for viewing.
    [MSD_FOOT_MAIN.DSN]
2020-12-10 Created function prototype and documentation.
2020-12-10 Added LED outputs to the state machine.
2020-12-13 Modified sensor reading for demo.
